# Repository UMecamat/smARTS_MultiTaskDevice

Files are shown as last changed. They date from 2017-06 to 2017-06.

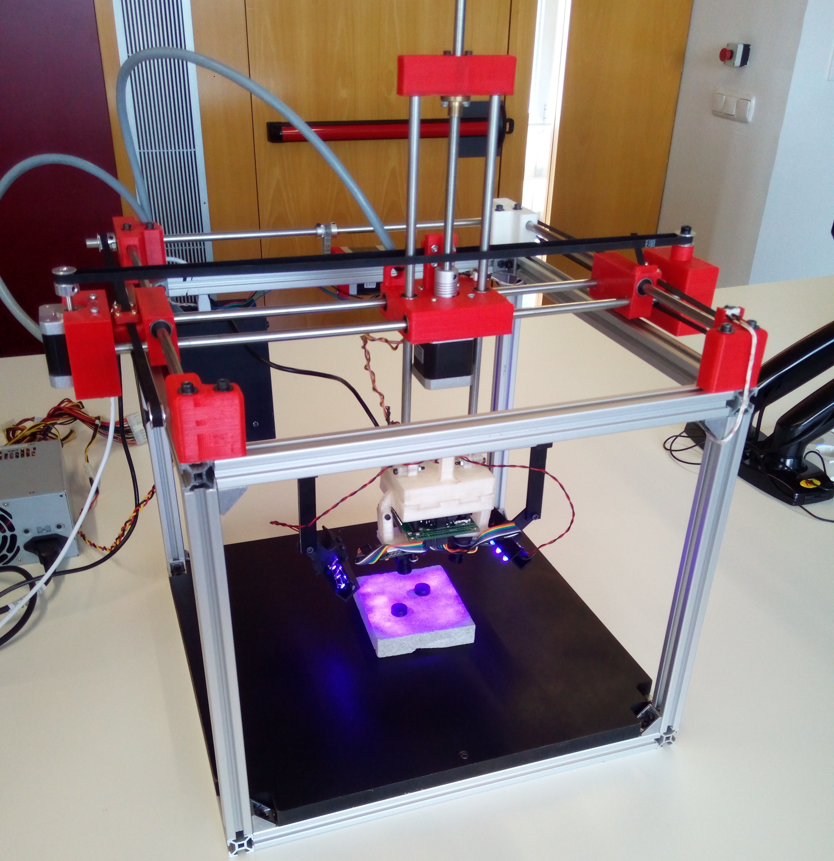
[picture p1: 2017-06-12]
smARTS Step by Step/Project_photo.jpg

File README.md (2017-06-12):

# smARTS
DEVELOPMENT OF AN ART ANALYSER AUTOMATED MACHINE 

smARTS is an Open Source project funded by the EU-Horizon 2020 research and innovations programme and is hosted by the MECAMAT research group. smARTS aims low cost prototypes, free and open source software and hardware technology for mapping, analyse and monitoring materials in the field of heritage science.

Our machine is based in a Cartesian movement system and its goal is to do a high resolution scanning of cultural heritage material samples, in order to map materials decay processes and patterns, and monitoring conservation treatments.

The project has been focused in order to be easy to replicate and assemble. It has been built with accessible and low cost materials. Moreover, it has been designed considering the chance to adapt the main dimensions to the user necessities, which makes it useful for a large community.

In this repository you can find the Step by Step Guide with all the information related with de development of this machine.
Enter in the smARTS Step by Step folder if you are interested in it.

Project Authors: Sergi Martínez, Marc Molet, Josep Pomés & Albert Rovira.

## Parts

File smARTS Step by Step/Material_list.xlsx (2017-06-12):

SmARTS
Material | Link | Unity Price | Quantity | Cost | Provider | Order Status | Total Cost | €226.30
Rexroth | http://www.motedis.es/shop/Perfil-Ranurado/Perfil-20-Tipo-B-ranura-6/Perfil-20x20-Tipo-B-Ranura-6::999991.html | €3.09 | 6 | €18.54 | Motoedis
Corners Rexroth + Fixation Game | http://www.motedis.es/shop/Accesorios-para-Perfil-Ranurado/Accesorios-Perfil-20-Tipo-B-Ranura-6/Escuadra-20-tipo-B-ranura-6::999991062.html | €0.66 | 24 | €15.84 | Motoedis
Trapezoidal nuts | http://www.motedis.es/shop/Accesorios-para-Perfil-Ranurado/Accesorios-Perfil-20-Tipo-B-Ranura-6/Tuerca-cabeza-martillo-tipo-B-ranura-6::99999555.html | €0.55 | 10 | €5.50 | Motoedis
Linear bearings 6x2 | http://www.3despana.com/rodamientos-y-guias/23-2-x-rodamiento-lineal-lm8uu.html | €1.89 | 6 | €11.34 | 3DEspana
Stainless steel rod | Alacer Mas | €1.36 | 6 | €8.16 | Alacer Mas
Synchronous Pulleys | http://www.3despana.com/poleas/368-polea-sincronizadora-dentada-gt2-5mm.html | €2.49 | 3 | €7.47 | 3DEspana
Transmission Pulleys A | http://www.3despana.com/mecanica/96-polea-dentada-8mm-para-gt2.html | €3.99 | 3 | €11.97 | 3DEspana
Transmission Pulleys B | http://www.3despana.com/mecanica/20-polea-dentada-5mm-para-gt2.html | €1.99 | 2 | €3.98 | 3DEspana
Belts 4mx2 | http://www.3despana.com/mecanica/21-1-metro-correa-nylon-gt2-6mm.html | €2.19 | 4 | €8.76 | 3DEspana
Stepper motors | http://www.3despana.com/motores/442-motor-nema-17-conector-17ah-42byghw609-4000gcm-.html | €10.99 | 3 | €32.97 | 3DEspana
PLA Coil | http://bcndynamics.com/ca/product/fil-pla-negre-carb%C3%B3-bq-175mm-1kg | €19.92 | 1 | €19.92 | BCNdynamics
Leadscreaw | http://www.3despana.com/husillos-varillaje/458-husillo-trapezoidal-roscado-300x8mm-p1-tuerca.html | €14.99 | 1 | €14.99 | 3DEspana
Lead Screaw Engine Coupler | http://www.3despana.com/mecanica/11-2-x-adaptador-flexible-coupling-5mm-8mm.html | €2.19 | 1 | €2.19 | 3DEspana
Arduino Mega | http://www.3despana.com/electronica/335-arduino-mega-mks-2560-premium.html | €24.99 | 1 | €24.99 | 3DEspana
Stepper motor drivers | http://www.3despana.com/drivers-stepstick-pololu/165-driver-stepper-drv8825-disipador.html | €3.19 | 3 | €9.57 | 3DEspana
Endstop | http://www.3despana.com/finales-de-carrera/309-final-de-carrera-mecanico-simpre.html | €0.69 | 6 | €4.14 | 3DEspana
Power supply | http://www.3despana.com/fuentes-de-alimentacion/76-fuente-de-alimentacion-12v-20a.html | €19.99 | 1 | €19.99 | 3DEspana
Igus bearing | http://www.ebay.es/itm/Igus-DryLin-R-RJ4JP-01-10-Linearlager-statt-LM10UU-3d-printer-linear-bearing-/201923263930?var= | 2.99 | 2 | €5.98 | Ebay

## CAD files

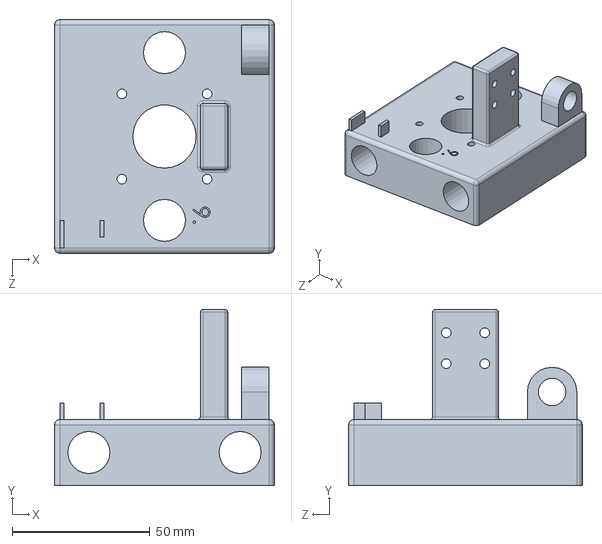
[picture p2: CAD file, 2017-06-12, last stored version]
9. Z axis Engine Support.SLDPRT
80.0 x 64.0 x 85.0 mm

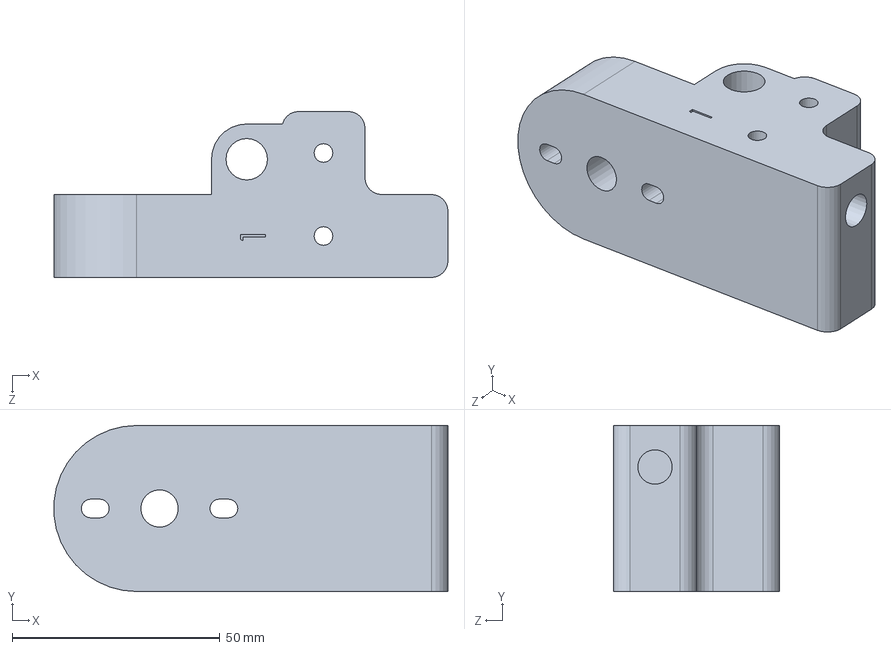
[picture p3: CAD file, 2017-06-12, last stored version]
1. Corner + bearing.SLDPRT
94.9 x 40.0 x 40.0 mm

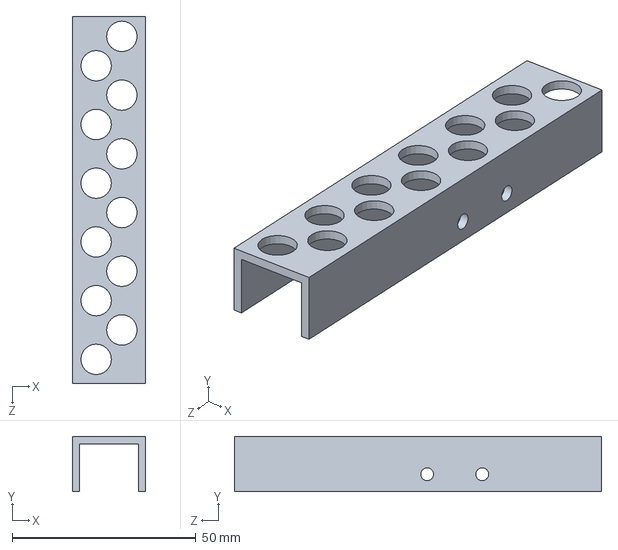
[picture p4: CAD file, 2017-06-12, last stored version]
19. LEDS.SLDPRT
20.0 x 15.0 x 100.0 mm

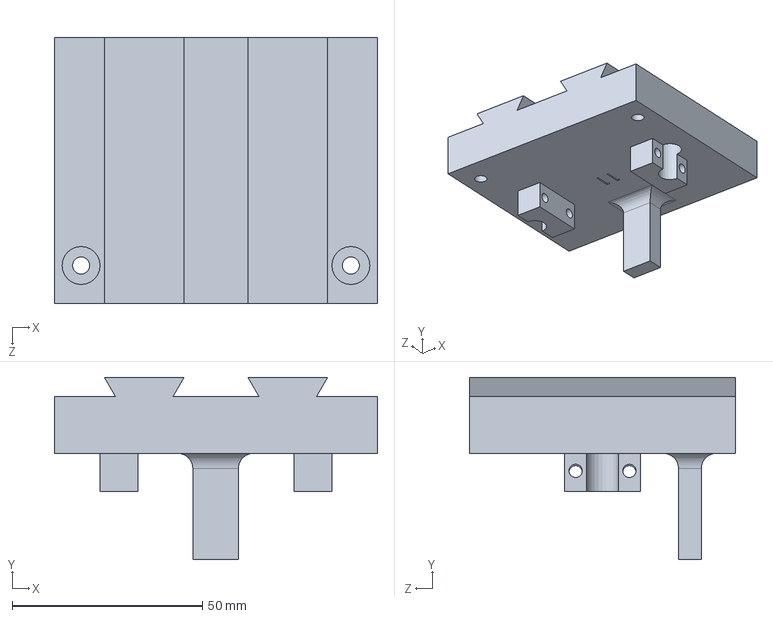
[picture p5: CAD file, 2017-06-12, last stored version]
11. Z axis Sensors Support.SLDPRT
85.0 x 48.0 x 70.0 mm

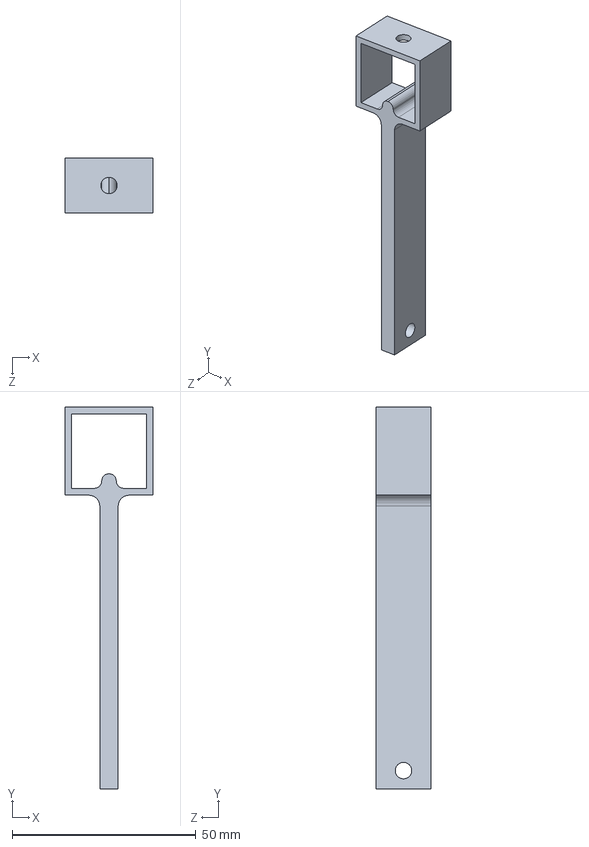
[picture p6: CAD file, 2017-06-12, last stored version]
17. LED 1.SLDPRT
24.0 x 104.0 x 15.0 mm

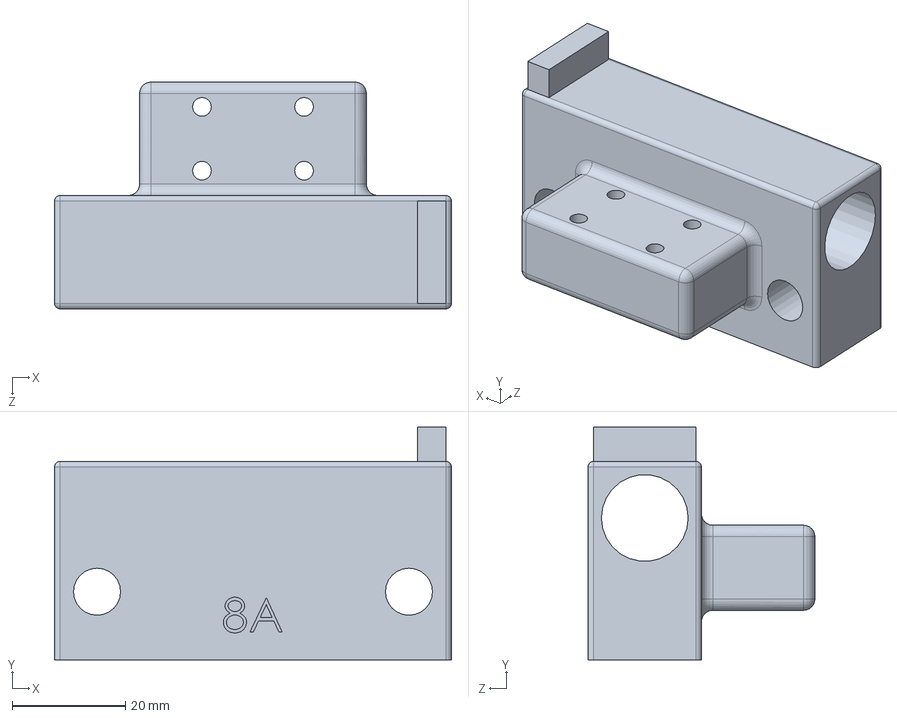
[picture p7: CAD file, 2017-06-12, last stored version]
8A. X-Y guide.SLDPRT
70.0 x 41.0 x 40.0 mm

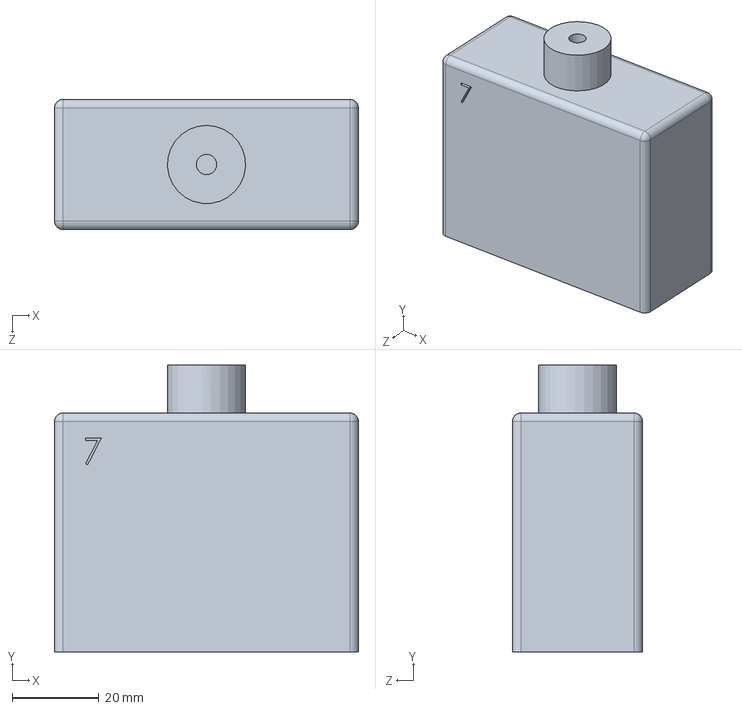
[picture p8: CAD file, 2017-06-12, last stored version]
7. X axis Counter Engine Support.SLDPRT
70.0 x 66.0 x 30.0 mm

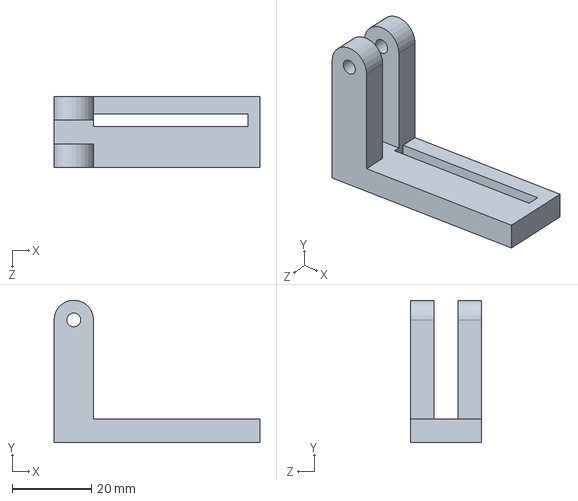
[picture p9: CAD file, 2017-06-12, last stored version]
16. Camera support A.SLDPRT
52.0 x 36.0 x 18.0 mm

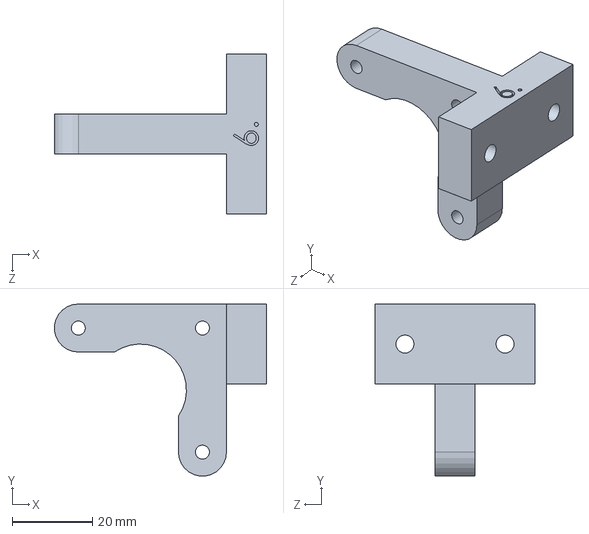
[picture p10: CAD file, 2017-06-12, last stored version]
6. Y axis Engine Support.SLDPRT
53.0 x 43.0 x 40.0 mm

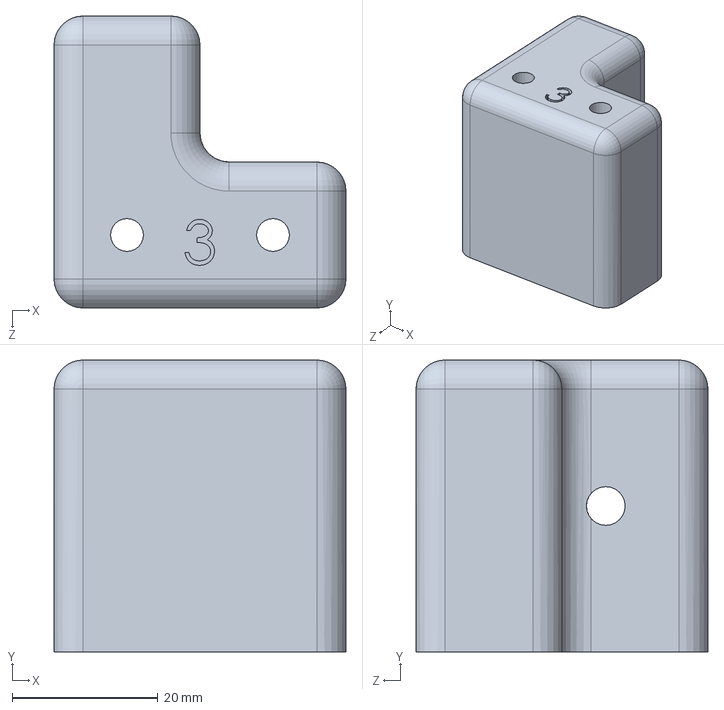
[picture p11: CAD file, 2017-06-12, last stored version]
3. Corner.SLDPRT
40.0 x 40.0 x 40.0 mm

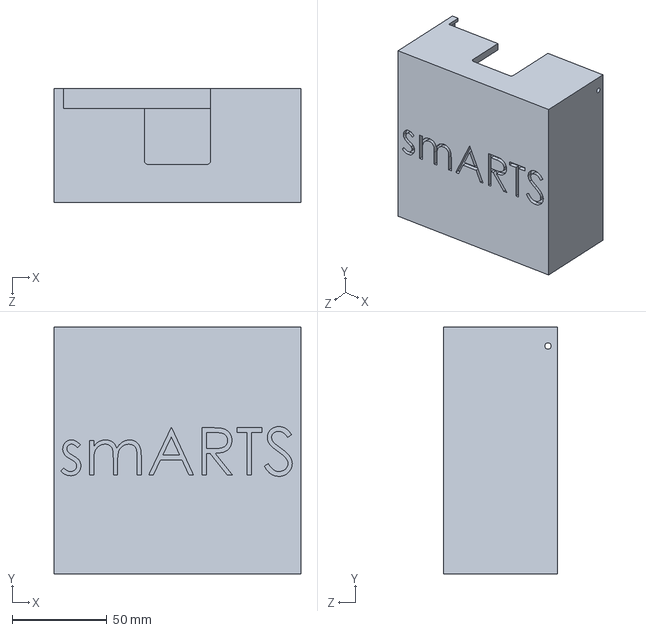
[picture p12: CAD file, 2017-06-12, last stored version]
13.1 Cover electronics.SLDPRT
130.0 x 130.0 x 60.0 mm

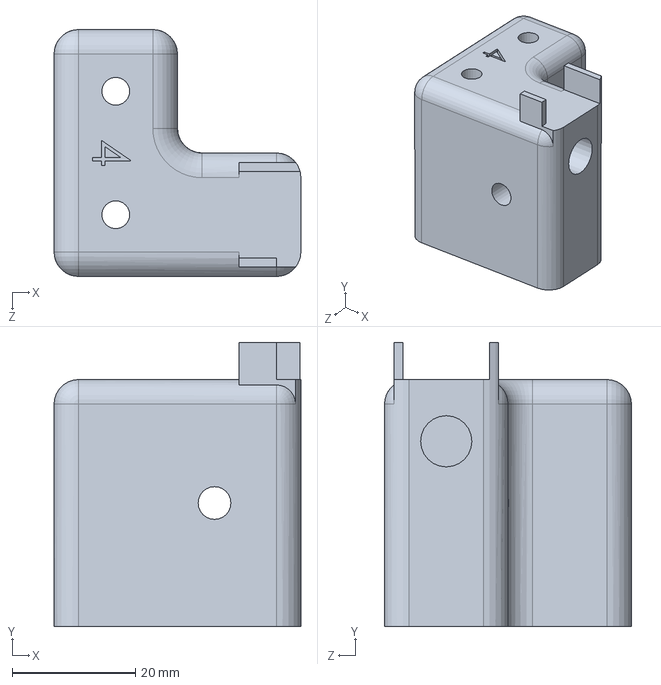
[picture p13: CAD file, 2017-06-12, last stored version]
4. Corner.SLDPRT
40.0 x 46.0 x 40.0 mm

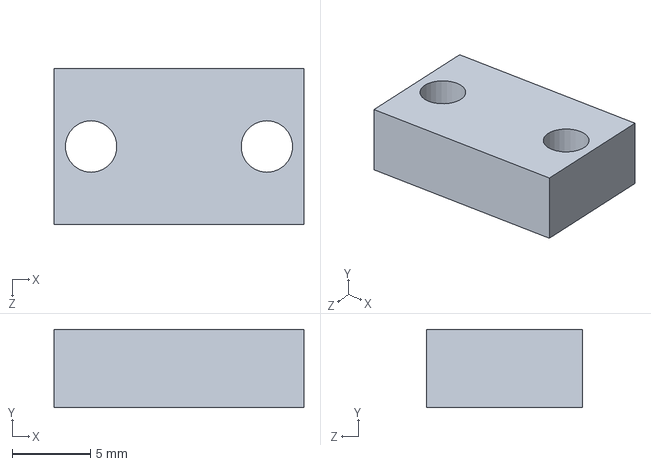
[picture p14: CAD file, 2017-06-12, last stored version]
12. Fix belt pices (x6).SLDPRT
16.0 x 5.00 x 10.0 mm

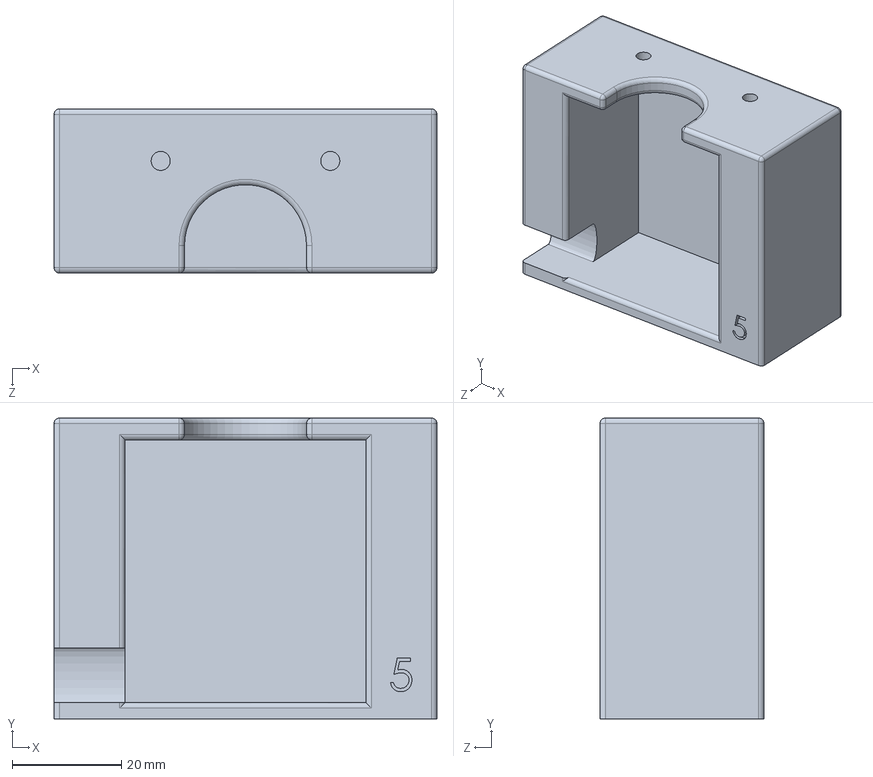
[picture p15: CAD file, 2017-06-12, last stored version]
5. X axis Engine Support.SLDPRT
70.0 x 55.0 x 30.0 mm

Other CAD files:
16. Camera support B.SLDPRT
13. Support electronica.SLDPRT
2. Corner + bearing.SLDPRT
8B. X-Y guide.SLDPRT
10. Z axis for Nut.SLDPRT
14. Secure support electronica (x2).SLDPRT
15. ArduinoUNO suport.SLDPRT
18. LED 2.SLDPRT

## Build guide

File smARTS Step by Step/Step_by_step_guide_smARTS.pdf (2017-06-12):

# DEVELOPMENT OF AN ART ANALYSER AUTOMATED MACHINE

### Step by Step Guide

### JUNE 2017

SERGI MARTÍNEZ, MARC MOLET, JOSEP POMÉS, ALBERT ROVIRA Universitat de Vic

Sergi Martínez, Marc Molet, Josep Pomés, Albert Rovira

## Step by Step Guide:

This is an automated machine able to move in the three Cartesian axis. You can control it with any PC via single movements or by programming a sequence.

Because it is oriented to analyse and map art samples, it has an easy-changing tool where different cameras and sensors are attached. We can also control some parameters such as the illumination.

### 1. Specifications

Before starting with the project, we would like to remark all the specifications of the Machine you will get after finishing this step by step guide.

Axis details:

- X-axis
- Travel: 240 mm
- Drive: Toothed Belt
- Speed: 30 mm/s (nominal)
- Acceleration: 900 mm/s²
- Resolution: 0.1 mm
- Y-axis
- Travel: 260 mm
- Drive: Toothed Belt
- Speed: 30 mm/s (nominal)
- Acceleration: 900 mm/s²
- Resolution: 0.1 mm
- Z-axis
- Travel: 180mm
- Drive: Leadscrew
- Speed: 10mm/s (nominal)
- Acceleration: 900 mm/s²
- Resolution: 0.1 mm

Other characteristics:
- Free and open source firmware and software.
- Fixed base (the motion of the Z-axis is not implemented in the base).
- Cheap and reused materials.
- Conventional manufacturing processes and 3D printing.
- The cost of the project will be lower than 250€.

### 2. Design and patterns

Our first concept of the prototype was that it had to be light and easy to replicate. Therefore, when we started translating our ideas into the computer we made the pieces thinking with the 3D impression.

The first stage of the drawing was to recreate with the Rexroth profiles all the edges of the cube.

Next, we began drawing the whole system for the horizontal movements X and Y, which we transform from the circular motion of the motors, to a linear movement through transmission belts.

Once we had the idea of the horizontal
movements, we started to implement the motor and the movement system of the Z axis (vertical). With the coupling of the worm screw fixed to the axis of the motor and through the nut of the screw worm, we converted the motor movement to a slow and precise vertical movement.

Up to this point, the structural design phase was implemented with all the possible movements and we simulated them with the computer to identify potential problems.

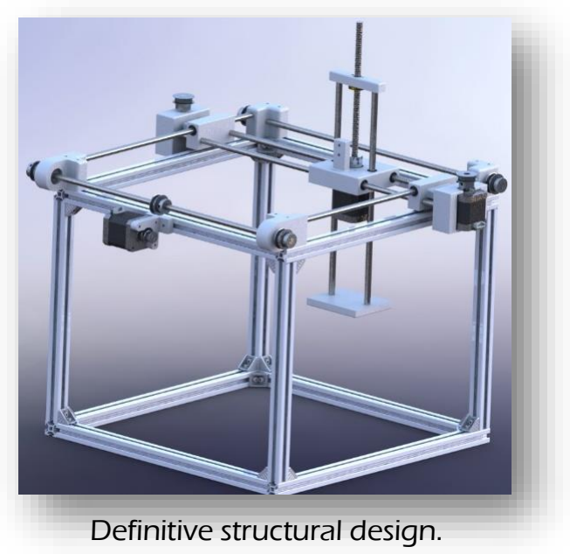
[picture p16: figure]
Definitive structural design.
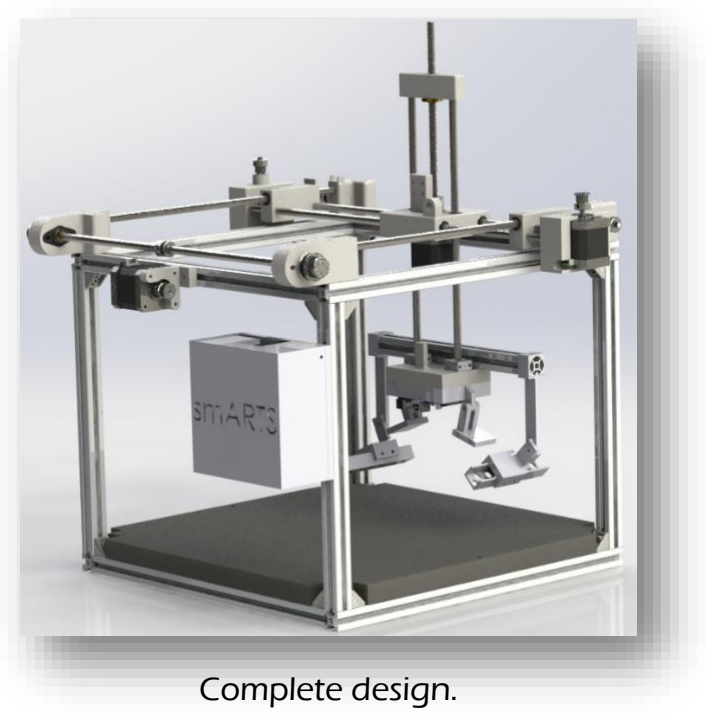
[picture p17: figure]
Complete design.

Once the three movements were tested it was the turn to design the head where the controller, cameras and led would go. We designed it to be completely modular and easy to implement different LED, cameras or sensors.

Finally, as we designed the pieces, we already thought about the time when we would create the step by step guide. We came up with the idea to facilitate the explanation and at the same time the assembly so we engrave the pieces with numbers to facilitate it.

### 3. Required Tools

To make the work more agile and not wasting so much time searching the necessary tools for a satisfactory assembly, we will provide a list of the necessary tools to facilitate the assembly. Besides in some tools we will propose alternative ones if the tool is not available.

Tool list:
3D Printer

It is the fundamental mainstay of the project. We need it to 3D-print all the parts before starting with the final assembling.

Tape measure

You might have heard the saying "measure twice, cut once". Well, you need a tape measure for measuring all the parts you will have to cut.

CNC milling machine / Hacksaw

On our case, we cut the rods and axes for the linear movement with a CNC milling machine for greater accuracy, but if in your workplace you do not have this machine, you can use a hacksaw. Be sure to have the exact measurements.

Screw drivers and Allen wrenches:

These two sets are necessary to unscrew and screw all those screws used in the union of parts and fixings.

Files:

Used to polish 3D printing imperfection and file the saw-cutted corners.

Pliers:

Different types of pliers are needed to hold the female for a more comfortable attachment of the screw.

Scissors:

Useful to cleanly cut the excess belts once assembled and peel the wires.

Glue gun:

It is not a necessary tool, but it can be useful for orderly fixing some annoying wire.

PPE (Personal Protection Equipment):

Do not forget in every mechanical assembly where cutting tools and sharp tools are used. Use the appropriate PPE in each situation.

### 4.Required materials

In this part, we will comment some materials used and the quantity we will need of each one. We will not enter in some details as the exact price and where to buy them. Trust us, they are very easy to find and we guarantee you that the cost will not exceed 250€ (if you look for them carefully you probably find all the material for around 200€).

If you want to know how to assemble the materials, please go to the following step.

To make the project reality, we will need to prepare these materials (check the document “Material List” to know the specifications of these materials):

- Rexroth (6m) | - Stepper motors (3 units)
- Rexroth Corners + Fixation Game (24 units) | - PLA Coil (1Kg)
- M3 and M4 Screws | - Lead Screw + nut (1 units)
- Engine Coupler Lead Screw (1 units) | - Linear bearings (10)
- Stainless steel rod (6m) | - Arduino Mega (1 units)
- Synchronous Pulleys - GT2 5mm (3 units) | - Belt-GT2 (4m)
- Transmission Pulleys A - GT2 8mm (3 units) | - Endstop (3 units)
- Transmission Pulleys B - GT2 5mm (2 units) | - Power supply (1 units)
- Stepper motor drivers-DRV8825 (3 units) | - Igus bearing (2 units)

Once we have the materials, we have to cut the Rexroth, the stainless steel rod and the lead screw, in specific measures to be able to proceed to the assembly, the rest of materials does not need be changed.

Rexroth measures:

- 4 bars of 400 mm
- 4 bars of 360 mm
- 4 bars of 300 mm
- 1 bar of 240 mm

Stainless steel rod measures:

- 2 bars of 500 mm
- 1 bar of 450 mm
- 2 bars of 370 mm
- 2 bars of 310 mm

Lead Screw measure:

- 1 bar of 200 mm (can be longer)

Now with all materials and tools prepared, we are ready to start with the assembling!

### 5. Assembling

In this step, we are going to explain in detail the building process.

Step 1
Materials needed:
Quantity: | Description
4 | Rextroth 400mm
4 | Rextroth 360mm
8 | Fixation Game
Description:
Take 2 Rextroth of 400mm and put them facing one each other, then take 2 Rextroth of 360mm and put them on the other side forming a perfect square, then take 4 fixation games and attach them one in each corner. Repeat this step once more in order to have 2 squares.
Step 2
Materials needed:
Quantity: | Description
4 | Rextroth 360mm
8 | Fixation game
Description:
Take one of the squares made in the Step 1, place each Rextroth of 360mm upwards each corner as shown in the image, then take 2 (per corner) fixation games and attach each the new Rexroths to the coincidence ones.

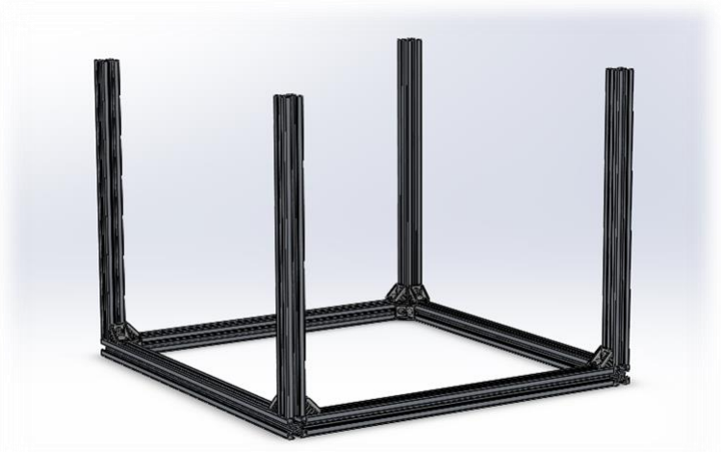
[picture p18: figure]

Step 3
Materials needed:
Quantity: | Description
8 | Fixation game
Description:
Take the assembly from the Step 2 and the remaining square from the Step 1, put the square above the assembly forming a cube, then use the fixation games to attach the square to the whole structure as shown in the image.
Step 4

Materials needed:
Quantity: | Description
1 | Piece 1
1 | Piece 2
4 | M4-45mm screw
4 | M4 T-nut
Description:
Take the structure from the Step 3, (note: the last square that have been attached must be facing up), look for one of the shorts Rexroths and place Pieces 1 and 2 in each corner facing each other, then attach each piece to the Rexroths using the M4 screws and the T-nut.

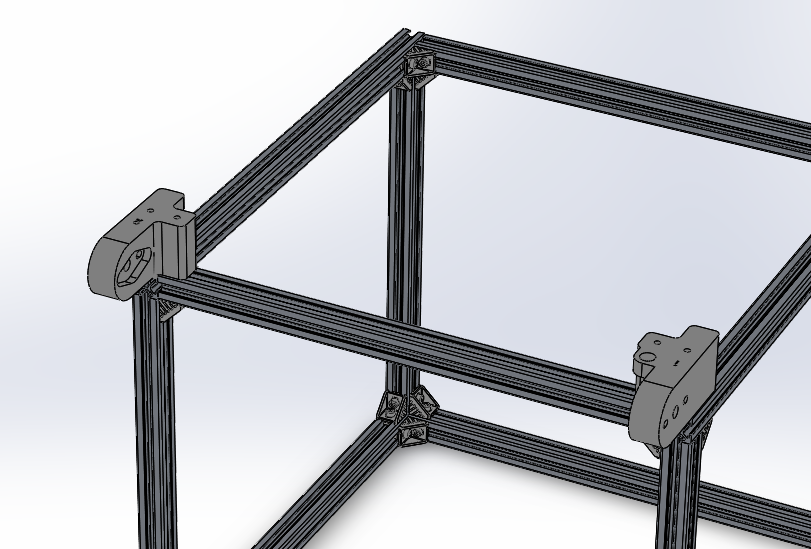
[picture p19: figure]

Step 5
Materials needed:
Quantity: | Description
1 | Piece 8A
1 | Piece 8B
1 | Piece 9
10 | Linear bearing
Description:
This step is for preparing the pieces 8A, 8B and 9. Firstly take a file and clean the holes of the pieces. Once the pieces has been cleaned take the linear bearings and put them inside the piece, the help of a nylon hammer may be needed.

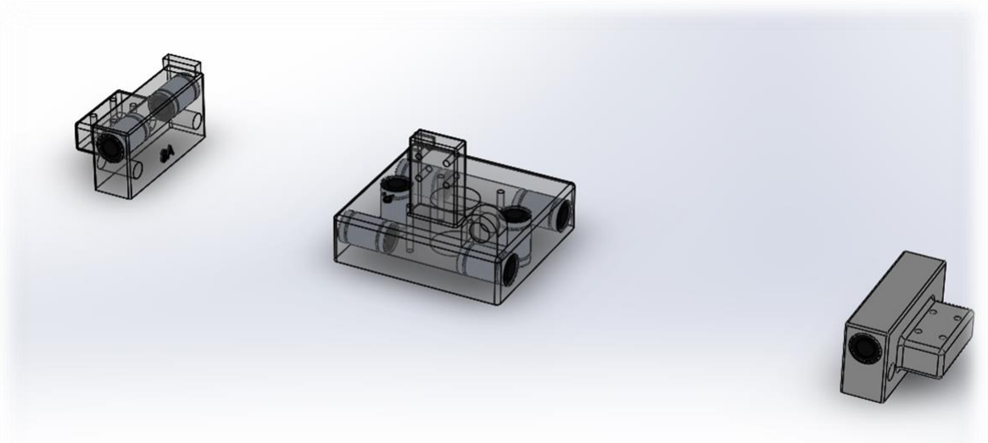
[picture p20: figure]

Here you can see in detail how the bearings need to be placed:

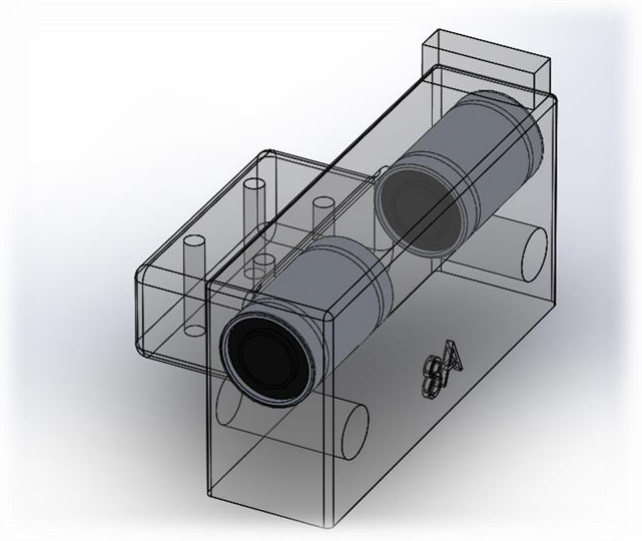
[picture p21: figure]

Step 6
Materials needed:
Quantity: | Description
2 | 8mm Rod-400mm
1 | Piece 5
1 | Piece 7
Description:
Take the pieces from the Step 5 and the two rods, firstly insert the rods into the free 8mm of the piece 8A, then slide the rods into the four lineal bearings placed into the piece 9, finally close the structure by inserting the piece 8B as shown in the second image.

Once that has been done, insert the outgoing part of the rod from the piece 8A into the holes of the piece 7.

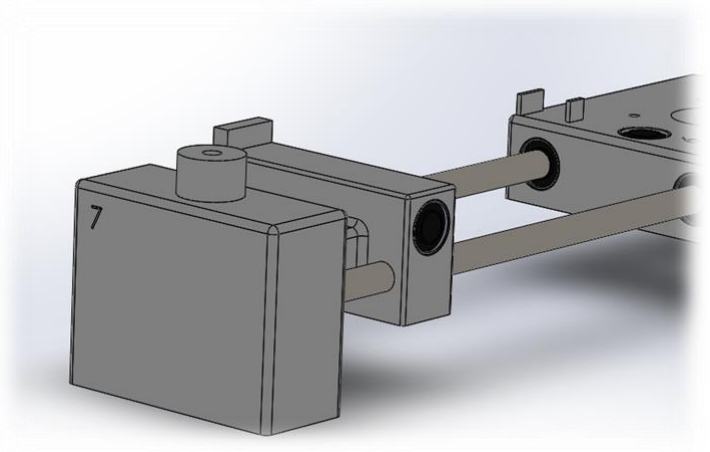
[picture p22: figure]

Finally, repeat the exact same process with the piece 5 in the other side.

Step 7
Materials needed:

Description:
Take the structure from the step 6, place the motor inside the piece 5 and then attach it by using two the two M3 screws, then place the 5mm transmission pulley into the motor shaft.

Once that has been done take the synchronous pulley and the M5 screw, attach the synchronous pulley directly into the top hole of the piece 7 (note: do not attach it to strong, the pulley must be able to move freely).

Step 8

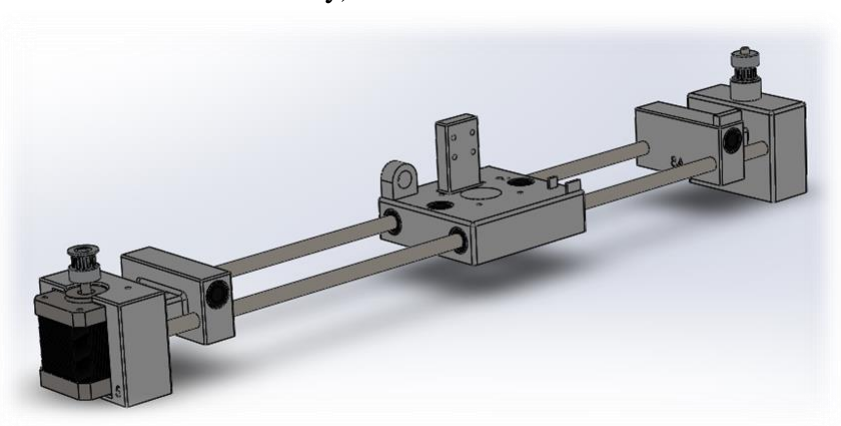
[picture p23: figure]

Materials needed:

Description:
In this step we are going to join the structure from the step 4 and the one from the step 7, for that take the two rods and place it into the holes of pieces 1 and 2, then put the structure from step 7 sliding the rods into the linear bearings from pieces 8A and 8B.
Quantity: | Description
1 | Nema 17 motor
1 | 5mm transmission pulley
1 | Synchronous pulley
2 | M3x10mm screws
1 | M5x50mm screw
Quantity: | Description
2 | 8mm Rod-370mm

Step 9
Materials needed:

Description:
To close the assembly got in the step 8 take the piece 3 and 4 and insert the outgoing rod from step 8 into the free hole of the pieces 3 and 4, then take the screws and the T-nuts and attach the pieces to the Rexroths.
Step 10

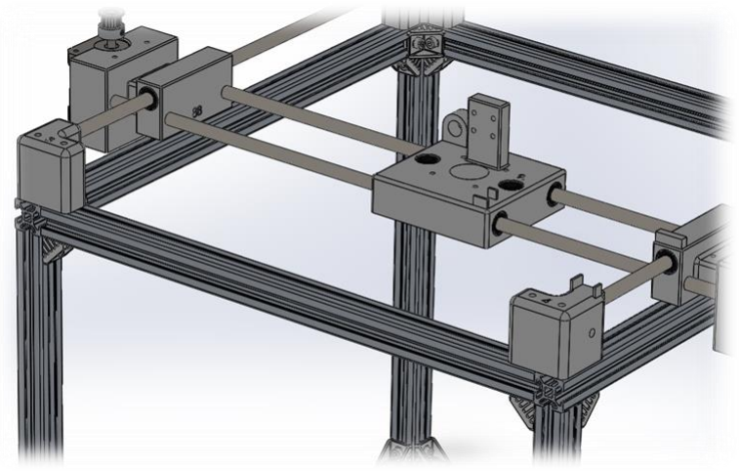
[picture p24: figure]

Materials needed:

Description:
Take the IGUS bearings and put each one into the piece 1 and 2, then take the screws and the nuts and attach them firmly to the piece.
Quantity: | Description
1 | Piece3
1 | Piece4
4 | M4x45mm screw
4 | M4 T-nut
Quantity: | Description
2 | IGUS bearing
4 | M4x25mmm screw
4 | M4 nut

Step 11
Materials needed:

Description:
Take the 8mm rod and pass it through the IGUS bearing, then put in their place (as shown in the image) the 8mm transmission pulleys and attach them in place.

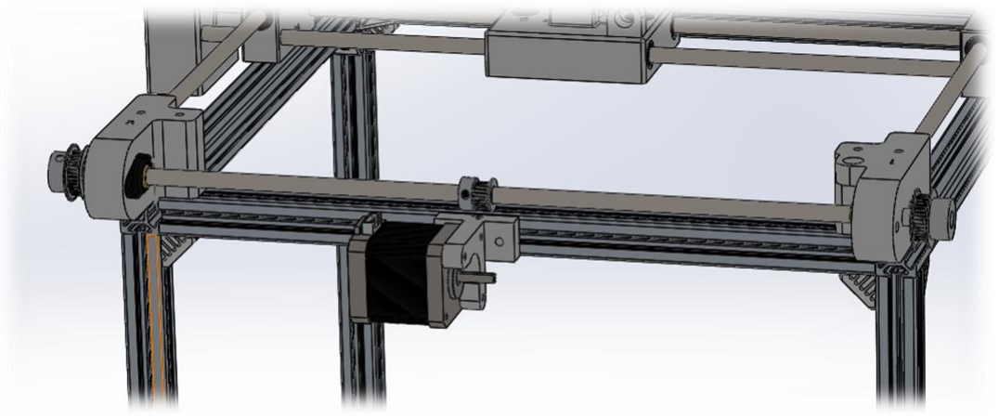
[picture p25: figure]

Take the piece 6 and attach it to the Rexroth by using the two M4 screws and the two T-nuts as shown in the image. Finally take the motor and attach it to the piece 6 by using the three M3 screws, then take the 5mm transmission pulley, place it into the motor shaft and attach it there.

Quantity: | Description
1 | Piece 6
1 | 8mm Rod-420mm
3 | 8mm transmission pulley
1 | 5mm transmission pulley
1 | Nema 17
1 | M4x15mm Screw
1 | M4x10mm Screw
2 | M4 T-nut

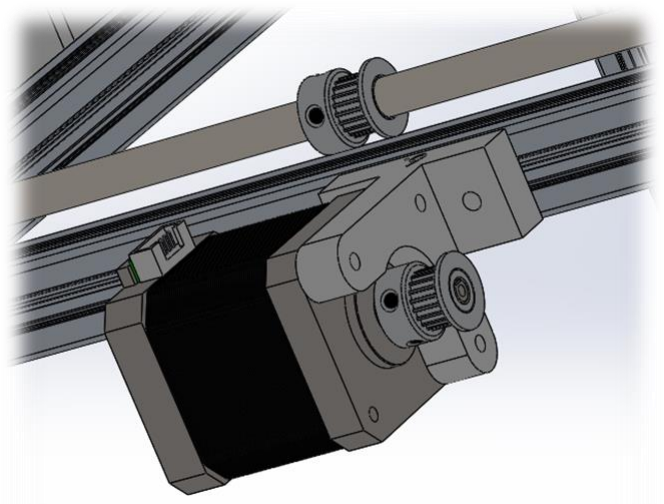
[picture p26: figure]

Step 12
Materials needed:

Description:
Take the synchronous pulleys and attach each one to the pieces 3 and 4 by using the screw and the autoblocking nut (note: do not attach it to strong, the pulley must be able to move freely).
Step 13
Materials needed:

Description:

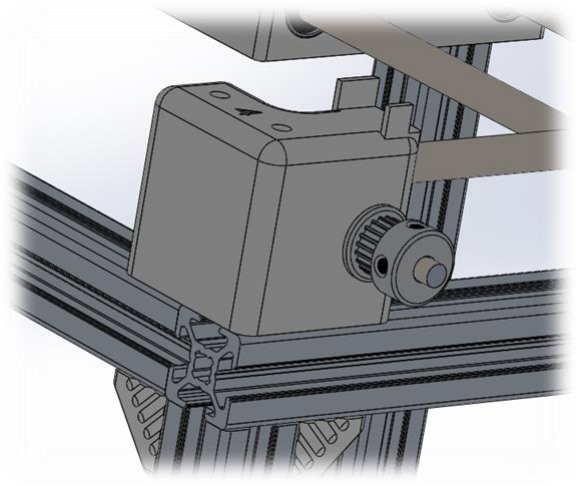
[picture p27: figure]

Take the shaft coupler and place it into the motor shaft, then attach it there, once that has done place the lead screw in the other hole of the shaft coupler and attach it there.

Quantity: | Description
2 | Synchronous pulley
2 | M5x45mm Screws
2 | M5 autoblocking nut
Quantity: | Description
1 | Nema 17
1 | Lead screw
1 | Shaft coupler

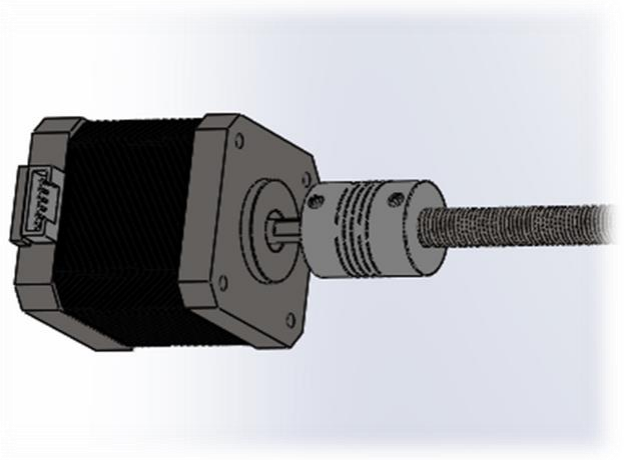
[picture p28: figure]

Step 14
Materials needed:

Description:
Take the assembly from the step 14 and place it inside the piece 9, attach the motor to the piece by using the 4 M3x30mm screws, then screw the lead screw nut into the main lead screw, finally take the two 8mm rods and pass them through the linear bearings inside piece 9.

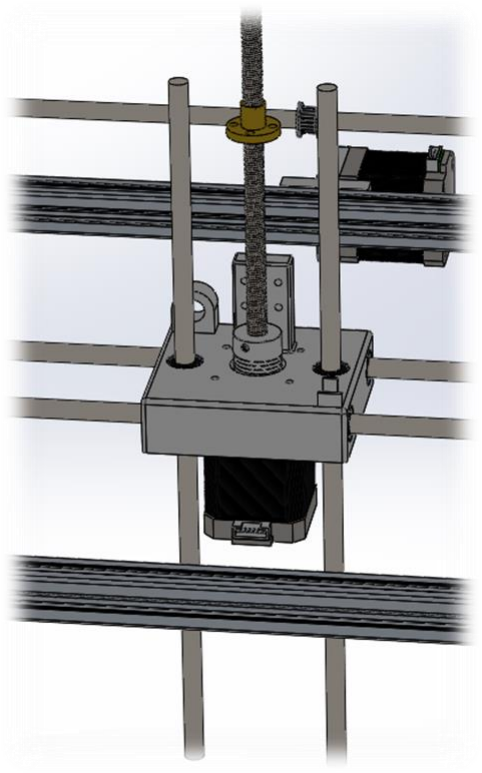
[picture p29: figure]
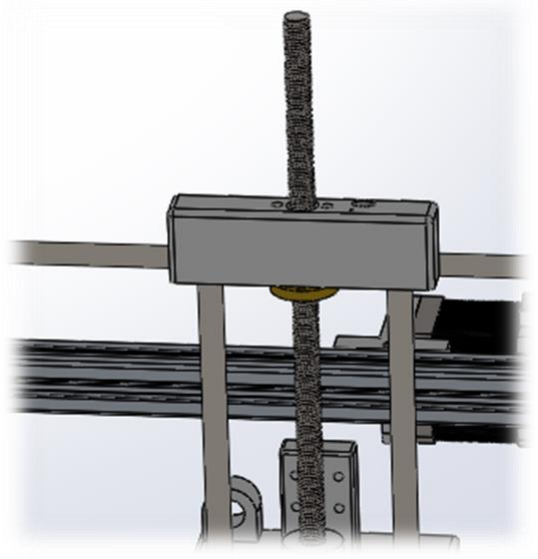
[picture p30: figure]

Finally join the rods and the lead screw nut by placing the piece 10, insert the 8mm rods into the free 8mm holes and then attach the nut by using the two M3x35mm Screws and the autoblocking nuts.

Quantity: | Description
1 | Lead screw nut
1 | Piece 10
2 | 8mm Rod-310mm
4 | M3x30mm Screws
2 | M3x35mm Screws
2 | M3 autoblocking nut

Step 15
Materials needed:

Description:
Take the piece 11 and place it under the assembly made in the step 13, insert the outgoing rods into the piece 11.

Finally put the brakets in place and tight the rods by compressing the brakets to the piece 11 using the M3 screws and the M3 nuts .

Quantity: | Description
1 | Piece 11
2 | BRAKETS
4 | M3x25mm Screw
4 | M3 nut

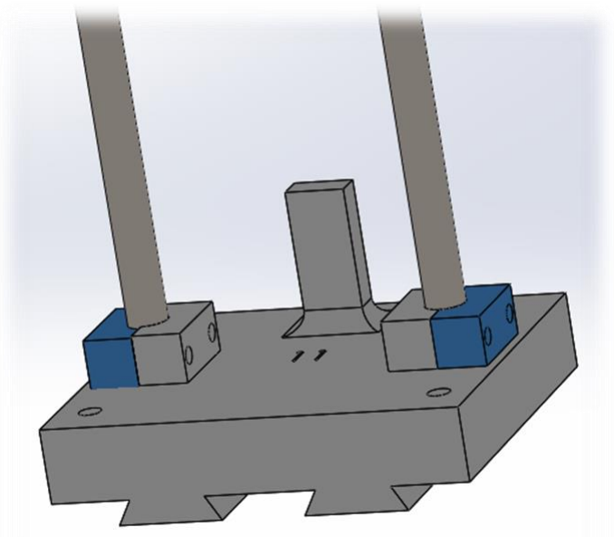
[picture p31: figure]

Step 16
Materials needed:

Description:
A board of wood 20mm thick needs to be cut following this pattern, to do that we did used the milling machine but it can be done by hand.
Quantity: | Description
1 | Wood Board

Step 16
Materials needed:

Description:
As the final step, all the wiring must be done and we just need to place the wood board at the bottom of the machine and then place all the electronics into the electronics box (see more about electronics in Electronics and Firmware Step).
Quantity: | Description
1 | Wood Board
1 | Electronics enclosure

Step 17
This is an extra step to show the configuration we have chosen for the lighting and the image acquisition, as this is a modular machine other designs can be implemented to fit the machine.

The lighting system we have design and tested is a directional one, which the X-axis and the angle of incidence can be moved and modified.

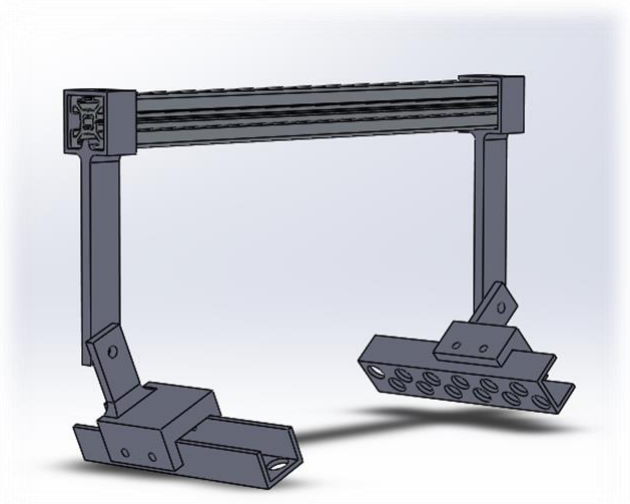
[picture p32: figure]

To get the image acquisition we have used the following system in which we have an Arduino UNO and two tilting arms where we can place the cameras.

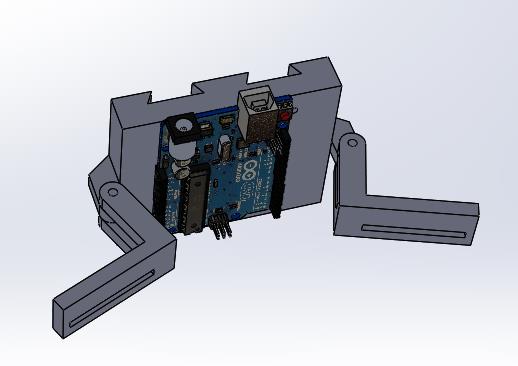
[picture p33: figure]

### 6. Electronics and Firmware

Electronics
About the electronics, as well as the whole project, the main objective was to develop an easy to replicate and open source board. That is the reason we´d chosen an Arduino as our main controller.

Arduino is an open source project which involves
different boards, so among all the variety we chose the

Arduino MEGA, the one in which we could upload the Marlin firmware.

Therefore, we had the necessity to joit all the components into a circuit, that’s the reason we have designed our own Circuit Board around the Arduino MEGA controller.

Required materials
Here you can see the materials needed to replicate the main board:
- Arduino MEGA (1 unit)
- DRV8825 stepper controller (3 units)
- ATX PC power supply (1 unit)
- Nema 17 stepper motor 400 steps per revolution (3 units)*
- End stop switch NO (3 units)*
- 1uF electrolytic capacitor (3 units)
- 1kΩ 1/4W resistor (4 units)
- Prototype perforated board 100mmx100mm (1 unit)
- Drivers stepper motors (3 units)
- IRF520N MOSFET (1 units)
- 330Ω 1/4W resistor (2 units per light system)*
- 3mm UV LED (10 units per light system)*
- Coper cable 0.75mm (10 meters)
- 2.54mm Male Pin (20 units)
- Arduino Mega (1 units)
*These components don’t go soldered directly to the main board

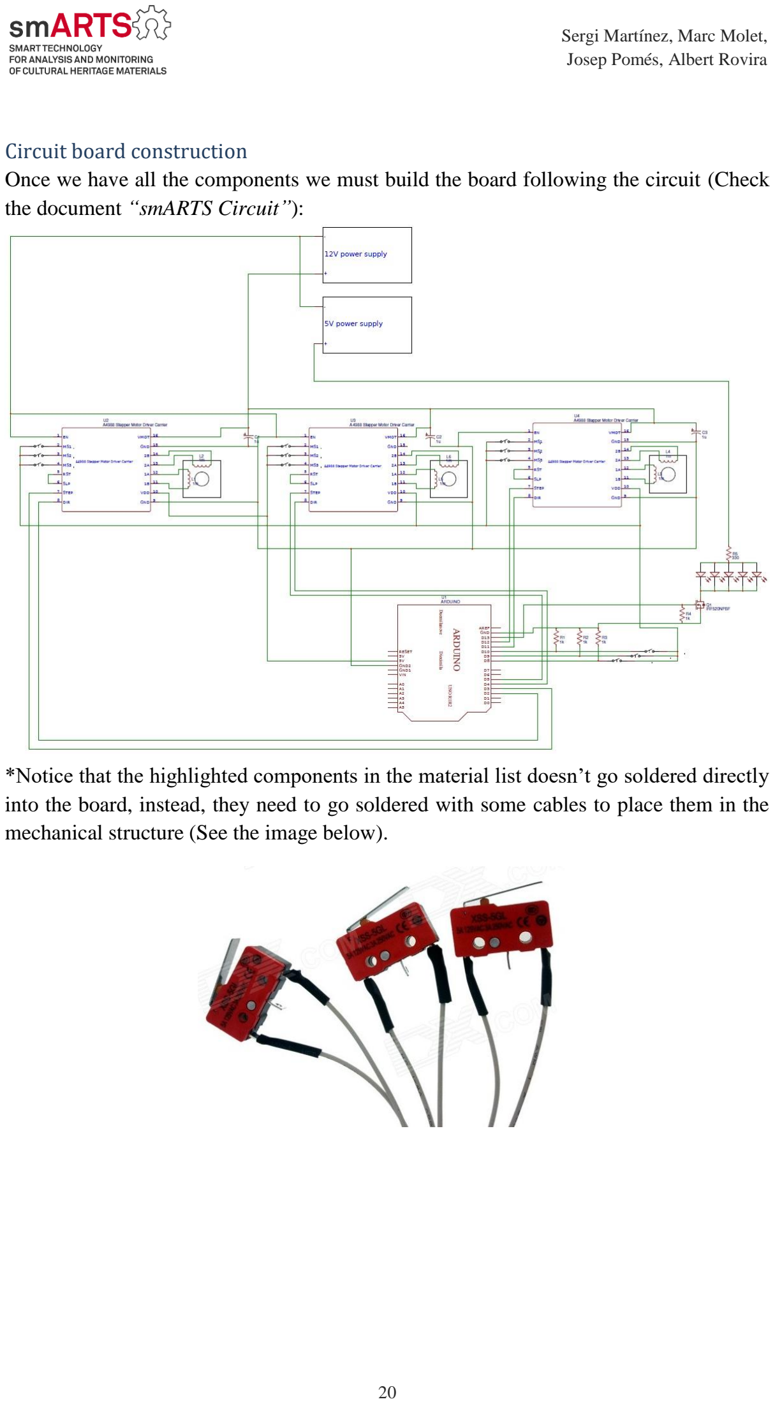
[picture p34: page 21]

Circuit board construction
Once we have all the components we must build the board following the circuit (Check the document “smARTS Circuit”):

*Notice that the highlighted components in the material list doesn’t go soldered directly into the board, instead, they need to go soldered with some cables to place them in the mechanical structure (See the image below).

Finally, here we can see the resulting board we got:

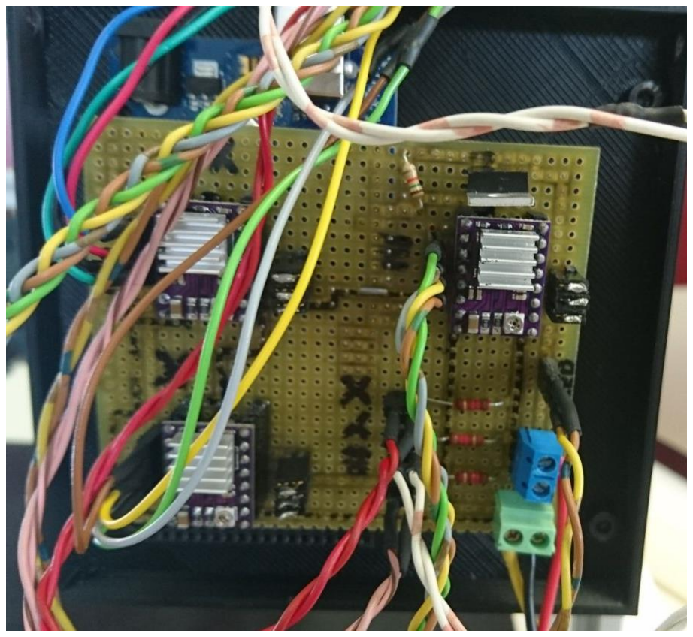
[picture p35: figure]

Seen the image, you can appreciate some extra features (which weren’t mandatory) we decided to add to make easier the job:

- Instead of soldering the motor driver directly to the board, we used some female connectors to change it easily in case they get burned.
- We also added some connectors for the power cables from the power supply.

Firmware
In order to have a working machine the Arduino Mega needs to run a code. The main objective of this code is to understand the
commands sent by the PC and move the
correspondent axis to the desired position.

Therefore, the firmware needed to run the Arduino has to be an universal G-Code interpreter, among all the variety we did found we decided to choose Marlin, and do the pertinent modifications in order to adapt it to our machine.

*The Modified version of the Marlin firmware can be found on smARTS GitHub site.

Here we are going to explain the changes we did to the original code.

Firstly, before doing nothing we got sure that the serial port the Arduino was using was the 0, and that the baud rate of the communication was able to be achieved by our PC program (250000bps is good enough).

Once we were sure about that we proceed to do the changes, the first one was to define the board as a: “BOARD_RAMPS_OLD”, this change has to be done in the Configuration.h tab.

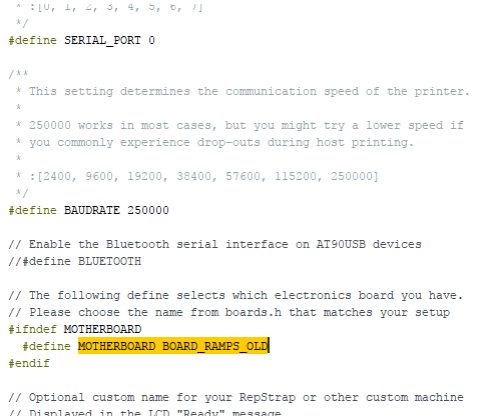
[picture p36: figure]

The second change we did was to comment the lines that enable the internal pull-ups of the controller in the pins we have the end stops, we did that because we already have an external pull-down in our circuit”, this change has to be done in the Configuration.h tab.

The third change we did was to set the inverting logic of all axis to false, this change has to be done in the Configuration.h tab.

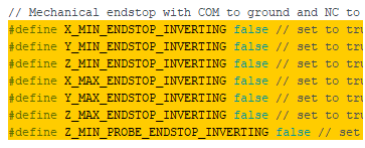
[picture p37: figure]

The fourth change we did was to define the steps per mm we had to give to the steppers, these values came from the combination of the numbers of teeth of the pulley, the steps per revolution of the motors and the microstepping from the drivers, this change has to be done in the Configuration.h tab.

The fifth change we did was to set the maximum acceleration of each axis to 1000mm/s^2, this change has to be done in the Configuration.h tab.

The last change we did was to set the pins were we connected the drivers and the end stops, this change has to be done in the pins_RAMPS_OLD.h tab.

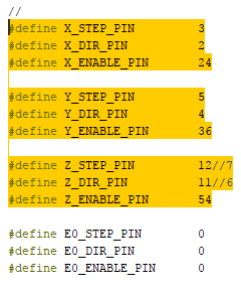
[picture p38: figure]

### 7. Controlling software:

Our controlling software will be Repetier-Host. It is a free programme available in Windows, Linux and Mac, which is compatible with most firmwares around.

With this GUI we will be able to move the tool in a very precise way, using the manual control menu or programming a sequence using G-code.

Here are the steps to follow if you want to use this software:

1. Download Repetier-Host from: https://www.repetier.com/download-software
2. Open the setup file, install the programme and run it.
3. Once running, go to Configuration → Printer settings and configure it with the

following parameters.

a. Connection:

Connector: Serial Connection

Port: Auto (or put your COM if you know it).

Baudrate: 250000

b. Printer:

Travel Feed Rate: 2000

Z-Axis Feed Rate: 17000

Invert Direction Controls for: Tick Z-Axis

c. Printer Shape:

Printer Type: Classic Printer

Home X: Max

Home Y: Min

Home Z: Min

Print Area Width: 260 mm

Print Area Depth: 240 mm

Print Area Height: 110 mm

4. Configuration done! Now plug the power supply and connect the Arduino USB

cable to the computer.

5. In the Repetier-Host main page press Connect to start using the machine.

Manual Control:
To use the manual control you should go to the Manual Control tab located on the top right. Once there you will see an easy control interface as the following one:
- Homing buttons: We use it to go to a single axis home position (first three) or to do a general homing (last one).
IMPORTANT! You must do a general homing every time you want to use the machine after it has been disconnected.
- Movement buttons: You can use it to move in the three axis in a distance between 0.1mm and 50mm.
- Speed multiplier: Moving this slider we can increase or reduce the nominal speed.
- “Fan” slider: In our case with this slider, we will activate/deactivate the illumination system and control the level of brightness.

Sequence mode:
To use this mode, you can import a G-code sequence or program your own.
- Importing a pre-created sequence:
You should go to File → Load and
select it. The G-code editor tab will be opened automatically.
- Create your own sequence: Go to the Print Preview tab on the top right. Once there press Edit G-code and
start coding.

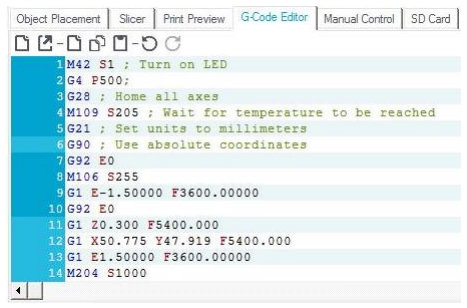
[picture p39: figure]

*If you need more information about G-code, we would like to recommend you to look for tutorials or visit the following webpage: http://reprap.org/wiki/G-code

### 8. smARTS useful links and repositories

Finally, we would like to invite you to the following web pages.

There you can download all the necessary archives and information if you want to replicate this project.

You also can be aware of the latest news related with the project or contact with us.

GitHub UMecamat:
https://github.com/UMecamat

smARTS Web Page:
https://smartsuvic.wixsite.com/smartsuvic

Youtube Channel:
https://www.youtube.com/channel/UCSC1kqYAXKj60nb-Jbjp_hg

Mecamat Web Page:
http://mon.uvic.cat/mecamat/smarts

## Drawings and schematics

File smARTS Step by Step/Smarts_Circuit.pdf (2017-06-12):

# 12V power supply

# 5V power supply

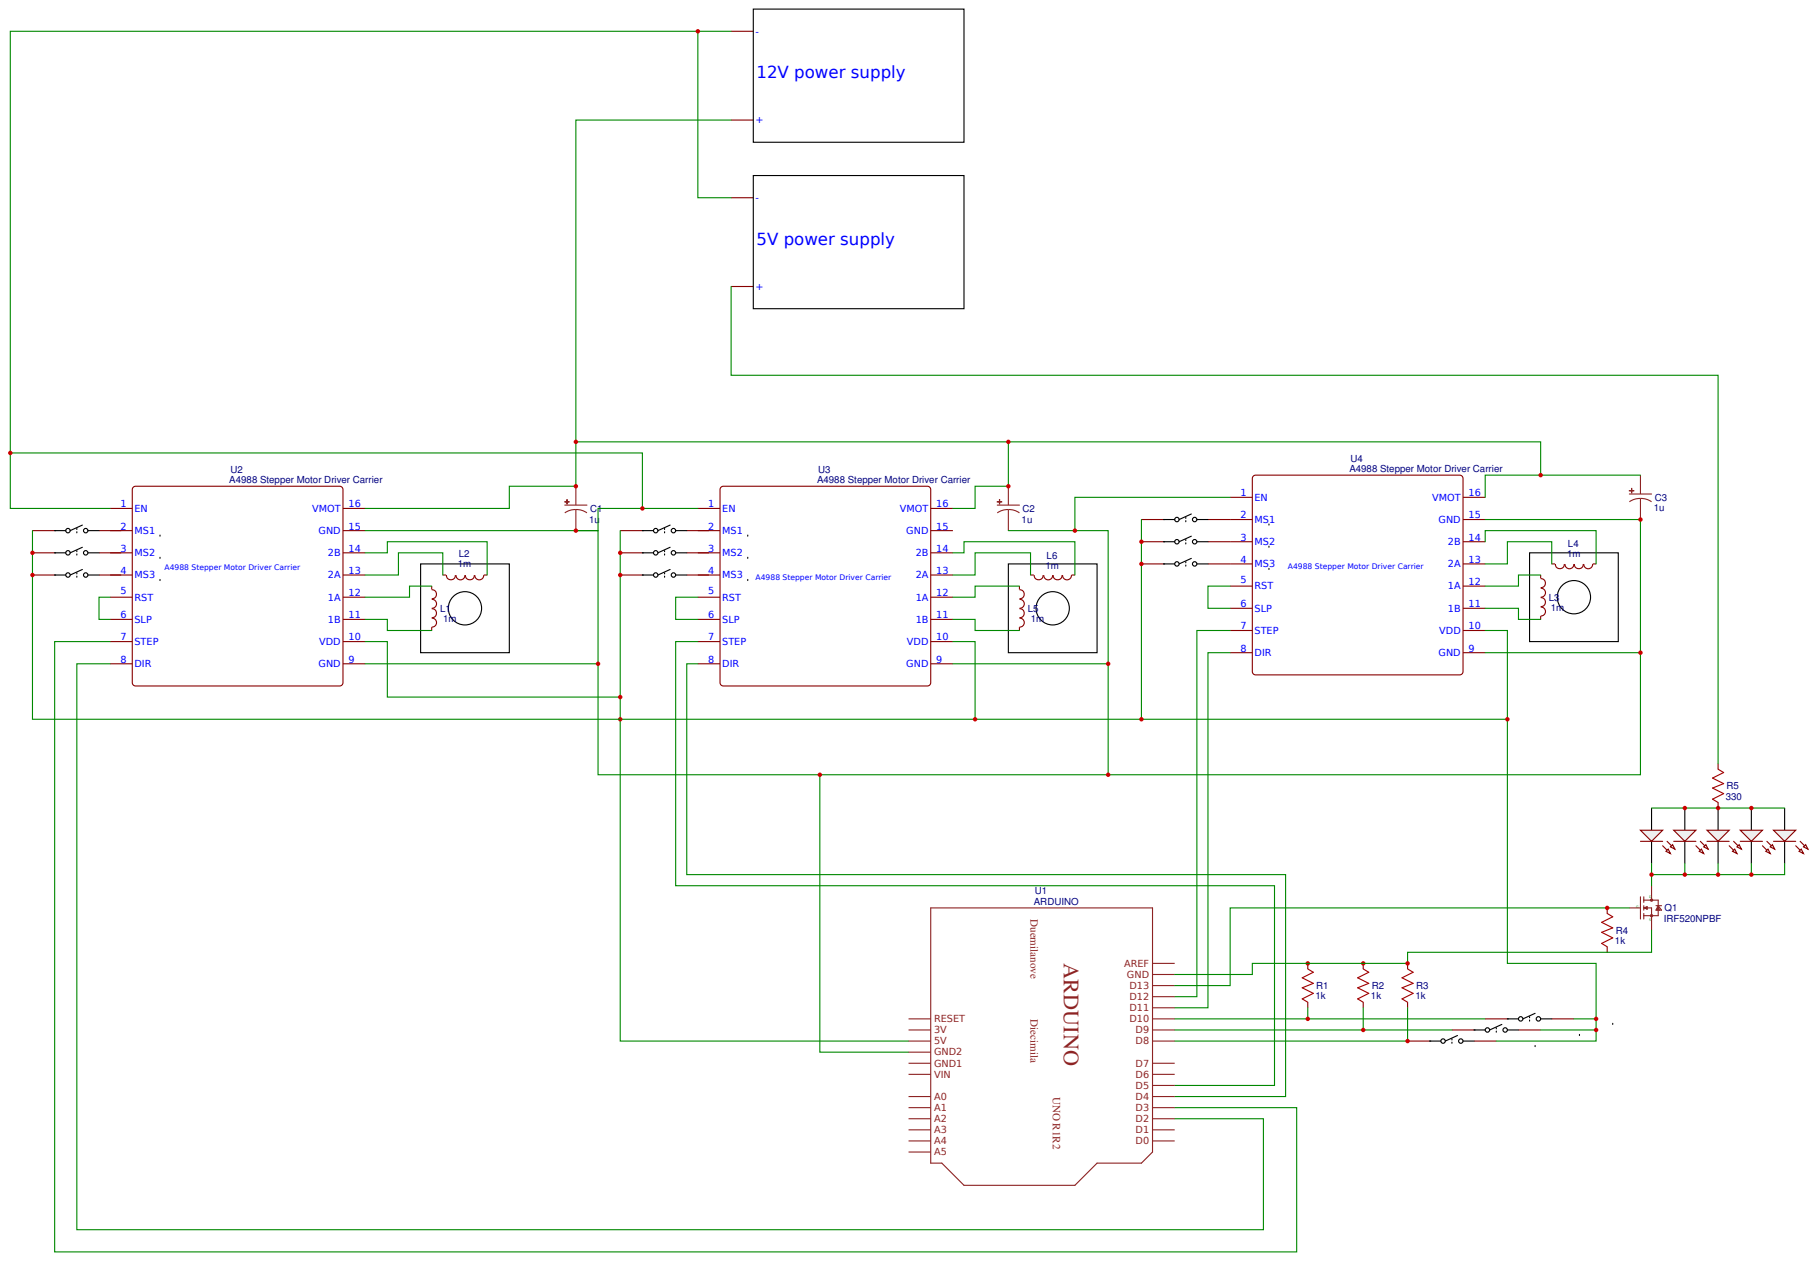
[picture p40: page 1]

A4988 Stepper Motor Driver Carrier
